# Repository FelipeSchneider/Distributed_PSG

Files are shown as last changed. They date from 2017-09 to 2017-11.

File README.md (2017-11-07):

# Distributed_PSG
Final project of the Electrical Engineering course, made by Felipe Britto Azevedo Schneider. The goal of this project is to develop hardware and software capable of monitoring a patient thought the night with more comfort that is possible using the traditional method.
Article abstract:
The impairment of sleep quality directly rises the chances of heart attack, obesity, and strokes, among others, what makes the polysomnography (PSG) an important public health tool. However, the inherent problems with PSG makes the correct diagnosis of sleep diseases a difficult task. This work presents a distributed novel class III PSG system, composed of three boards, all together capable of monitoring simultaneously environmental variables and patient signals. This system reduces the distress of a PSG exam, dismiss the need for an overnight sleep in a health care/sleep center, facilitates a self-set-up and an internet based diagnosis. Methods: Design and implementation of two wearable and one bedside PCB boards that together are able to, synchronously, monitor, process and log into a microSD card environmental parameters (temperature, humidity, visible light intensity and audible noise level) together with patient signals (electrocardiogram, electrooculogram, body, and limbs position). Results: A novel class III PSG system with independent boards capable of operating for more than 16 hours powered by a 750 mAh, 3.7 V battery with 0.003% data loss during preliminary PSG exams. Additionally, a computer-based program capable of reading, decode and present the data in graphs was developed and is presented. Conclusion: This article contributes to the PSG research and with the development of new PSG systems as well as the improvement of patients comfort. All code and hardware here developed are open.

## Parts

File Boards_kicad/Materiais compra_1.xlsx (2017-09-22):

MOUSER OU DIGIKEY |  |  |  |  | COMPRA NO BRASIL / JÁ COMPRADO ALIEXPRESS |  |  |  |  | AMOSTRA TEXAS
Encapsulamento | Quantity | Designation | Preço un | Total | Encapsulamento | Quantity | Designation | Preço un | Total | Encapsulamento | Quantity | Designation | Preço un | Total
TQFP-100_14x14mm_Pitch0.5mm | 1 | ATXMEGA128A1U-A |  |  | Pin_Header2x05 | 3 | PORT A |  |  | SC-70-5 | 1 | TPS71727
 |  |  |  |  | Pin_Header2x02 | 1 | CONN_02X02 |  |  | SC-70-5 | 1 | TPS71733
 |  |  |  |  | Pin_Header2x03 | 1 | PDI |  |  | ADXL335 | 1 | ADXL335
 |  |  |  |  | Pin_Header1x02 | 5 | CONN_01X02 |  |  | ADS1293 | 1 | ADS1293
 |  |  |  |  | Pin_Header1x10 | 1 | nRF8001 CON |  |  | HDC1000 | 1 | HDC1000
R_0603 | 4 | 1K2 |  |  |  |  |  |  |  | OPT3001 | 1 | OPT3001
R_0603 | 3 | 47k
R_0603 | 2 | 15k |  |  | TO-92 | 2 | LM35
R_0603 | 8 | 10K
R_0603 | 1 | 8k2
R_0603 | 4 | 220 |  |  | Trimpot | 1 | 100k
R_0603 | 3 | 1M
R_0603 | 1 | 120k |  |  | LDR | 1 | LDR
R_0603 | 6 | 100k
R_0603 | 1 | 12k |  |  | J2-connector | 3 | MIC-CON-MONO
R_0603 | 1 | 180k |  |  | 5mm-smd-button | 1 | SW_PUSH
R_0603 | 2 | 10k |  |  | 4.5mm-dip-button | 1 | SW_PUSH
R_0603 | 1 | 22k
C_0603 | 5 | 10nF |  |  | Diode_DO-35 | 1 | D_Schottky
C_0603 | 15 | 100n |  |  | Diode_DO-41 | 2 | D_Schottky
C_0603 | 4 | 10uF |  |  | Eletret-mic-6x5 | 1 | Electret-mic
C_0603 | 7 | 1uF
C_0603 | 3 | 10u
C_0603 | 2 | 22p |  |  |  |  |  |  |  | DBV-PDSO-G6 | 1 | LM2665
C_0603 | 1 | 1u |  |  |  |  |  |  |  | SOIC8-PDSO_G8 | 1 | opa2333
C_0603 | 2 | 100nF
C_0603 | 6 | Xn
C_0603 | 1 | 1.5n
C_0603 | 3 | 3u3
C_0603 | 1 | 16pF
C_0603 | 2 | 2u2F
C_0603 | 2 | 1u5F
Diode_DO-35_SOD27_Horizontal_RM10 | 1 | Z 5.7V
LED_0603 | 4 | LED
uSD_5027_normal | 1 | uSD
Crystal_HC49-U_Vertical | 1 | 4.096MHz
R_0805 | 2 | FILTER

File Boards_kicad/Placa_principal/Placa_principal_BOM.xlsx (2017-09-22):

Id | Designator | Package | Quantity | Designation | Supplier and ref | posicionados
1 | R25 | R_0603 | 1 | 100K |  | R25
2 | R19,R22,R23,R24 | R_0603 | 4 | 1K2 |  | R19, R22
3 | ,, | 1pin | 3
4 | P4 | Pin_Header_Straight_2x05 | 1 | PORT A
5 | C16,C2,C5,C13,C33 | C_0603 | 5 | 10nF |  | C2,C5,C22
6 | C37,C22,C23,C32,C35,C36,C38,C39,C40,C41,C42,C43,C44,C45,C46 | C_0603 | 15 | 100n |  | C35,C23,C32
7 | P6 | Pin_Header_Straight_2x05 | 1 | PORT D
8 | U3,U1 | TO-92_Molded_Narrow_Oval | 2 | LM35
9 | X1 | Crystal_HC49-U_Vertical | 1 | 4.096MHz
10 | IC1 | TQFP-100_14x14mm_Pitch0.5mm | 1 | ATXMEGA128A1U-A
11 | C9,C10,C14,C17 | C_0603 | 4 | 10uF
12 | C1,C3,C4,C6,C7,C8,C15 | C_0603 | 7 | 1uF |  | C1,C3,C4,C6,C7
13 | C11,C12,C20 | C_0603 | 3 | 10u |  | C20
14 | C18,C19 | C_0603 | 2 | 22p |  | C18,C19
15 | C21 | C_0603 | 1 | 1u
16 | C24,C25 | C_0603 | 2 | 100nF
17 | C26,C27,C28,C29,C30,C31 | C_0603 | 6 | Xn
18 | C34 | C_0603 | 1 | 1.5n |  | C34
19 | D1 | Diode_DO-35_SOD27_Horizontal_RM10 | 1 | Z 5.7V
20 | D2,D3,D4,D5 | LED_0603 | 4 | LED |  | D2,D3,D4,D5
21 | FB1,FB2 | R_0805 | 2 | FILTER
22 | P1 | Pin_Header_Straight_2x02 | 1 | CONN_02X02
23 | P3 | Pin_Header_Straight_2x03 | 1 | PDI
24 | P5 | Pin_Header_Straight_2x05 | 1 | PORT J
25 | P8 | Pin_Header_Straight_1x10 | 1 | nRF8001 CON
26 | R1,R2,R33 | R_0603 | 3 | 47k
27 | R3,R4 | R_0603 | 2 | 15k
28 | R5,R12,R13,R14,R15,R16,R17,R26 | R_0603 | 8 | 10K |  | R12,R13,R14,R15,R16,R17
29 | R7 | R_0603 | 1 | 8k2
30 | R8,R9,R10,R11 | R_0603 | 4 | 220 |  | R8,R9,R10,R11
31 | R18,R20,R21 | R_0603 | 3 | 1M |  | R18,R21
32 | U2 | SC-70-5 | 1 | TPS71727
33 | U4 | SC-70-5 | 1 | TPS71733
34 | U5 | ADXL335 | 1 | ADXL335 |  | X
35 | U6 | ADS1293 | 1 | ADS1293 |  | X
36 | U7 | HDC1000 | 1 | HDC1000 |  | X
37 | U8 | OPT3001 | 1 | OPT3001
38 | VR1 | Pin_Header_Straight_1x03 | 1 | 100k
39 | P15,P12,P13,P14,P16 | Pin_Header_Straight_1x02 | 5 | CONN_01X02
40 | R6 | Pin_Header_Straight_1x02 | 1 | LDR
41 | SD1 | uSD_5027_normal | 1 | uSD |  | SD1
42 | P9,P10,P11 | J2-connector | 3 | MIC-CON-MONO |  | P9,P10,P11
43 | SW1 | 5mm-smd-button | 1 | SW_PUSH |  | SW1
44 | SW2 | 4.5mm-dip-button | 1 | SW_PUSH |  | SW2
45 | C47,C48,C49 | C_0603 | 3 | 3u3 |  | c47,c49
46 | C50 | C_0603 | 1 | 16pF |  | C50
47 | C51,C54 | C_0603 | 2 | 2u2F |  | C51,C54
48 | C52,C53 | C_0603 | 2 | 1u5F |  | C52,C53
49 | D6 | Diode_DO-35_SOD27_Horizontal_RM10 | 1 | D_Schottky
50 | D7,D8 | Diode_DO-41_SOD81_Vertical_AnodeUp | 2 | D_Schottky
51 | MK1 | Eletret-mic-6x5 | 1 | Electret-mic
52 | R27 | R_0603 | 1 | 120k
53 | R28,R29,R30,R32,R36 | R_0603 | 5 | 100k
54 | R31 | R_0603 | 1 | 12k
55 | R34 | R_0603 | 1 | 180k
56 | R35,R38 | R_0603 | 2 | 10k
57 | R37 | R_0603 | 1 | 22k
58 | U9 | DBV-PDSO-G6 | 1 | LM2665
59 | U10 | SOIC8-PDSO_G8 | 1 | opa2333

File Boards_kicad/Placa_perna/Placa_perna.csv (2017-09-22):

Id | Designator | Package | Quantity | Designation | Supplier and ref
1 | C1,C2,C4,C7,C9 | C_0603 | 5 | 1uF
2 | C3,C6 | C_0603 | 2 | 10nF
3 | C10 | C_0603 | 1 | 10u
4 | C11 | C_0603 | 1 | 100nF
5 | C12,C13,C14 | C_0603 | 3 | 100n
6 | D1 | Diode_DO-35_SOD27_Horizontal_RM10 | 1 | Z 5.7V
7 | D2,D3 | LED_0603 | 2 | LED
8 | P1,P5 | Pin_Header_Straight_1x02 | 2 | CONN_01X02
9 | P3 | Pin_Header_Straight_2x03 | 1 | PDI
10 | P4 | 4-pin-50mil | 1 | CONN_01X04
11 | P6 | Pin_Header_Straight_1x10 | 1 | nRF8001 CON
12 | R1,R3 | R_0603 | 2 | 47k
13 | R4 | R_0603 | 1 | 10K
14 | R5,R6 | R_0603 | 2 | 220
15 | SD1 | uSD_5027_normal | 1 | uSD
16 | SW1 | 5mm-smd-button | 1 | SW_PUSH
17 | U2 | SC-70-5 | 1 | TPS71733
18 | U3 | SC-70-5 | 1 | TPS71727
19 | U4 | ADXL335 | 1 | ADXL335
20 | IC1 | TQFP-44_10x10mm_Pitch0.8mm | 1 | ATXMEGA128A4U-A
21 | P2 | 2x2-pin-50mil | 1 | CONN_02X02
22 | , | 1pin-mod | 2 | 1pin

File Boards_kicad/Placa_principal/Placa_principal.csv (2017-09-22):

Id | Designator | Package | Quantity | Designation | Supplier and ref
1 | C14,C9,C10,C17,C58 | C_0603 | 5 | 10uF
2 | U7 | HDC1050 | 1 | HDC1050
3 | C34 | C_0603 | 1 | 1.5n
4 | R25 | R_0603 | 1 | 100K
5 | R19,R22,R5,R12,R13,R14,R15,R16,R17,R23,R24,R26 | R_0603 | 12 | 10K
6 | P4 | Pin_Header_Straight_2x05 | 1 | PORT B
7 | C16,C2,C5,C13,C33 | C_0603 | 5 | 10nF
8 | C37,C22,C23,C32,C35,C36,C38,C39,C40,C41,C42,C43,C44,C45,C46,C56,C57 | C_0603 | 17 | 100n
9 | P6 | Pin_Header_Straight_2x05 | 1 | PORT D
10 | U3,U1 | TO-92_Molded_Narrow_Oval | 2 | LM35
11 | X1 | Crystal_HC49-U_Vertical | 1 | 4.096MHz
12 | IC1 | TQFP-100_14x14mm_Pitch0.5mm | 1 | ATXMEGA128A1U-A
13 | C1,C3,C4,C6,C7,C8,C15 | C_0603 | 7 | 1uF
14 | C11,C12,C20 | C_0603 | 3 | 10u
15 | C18,C19 | C_0603 | 2 | 22p
16 | C21 | C_0603 | 1 | 1u
17 | C24,C25 | C_0603 | 2 | 100nF
18 | C26,C27,C28,C29,C30,C31 | C_0603 | 6 | Xn
19 | D2,D3,D4,D5 | LED_0603 | 4 | LED
20 | P1 | Pin_Header_Straight_2x02 | 1 | CONN_02X02
21 | P3 | Pin_Header_Straight_2x03 | 1 | PDI
22 | P5 | Pin_Header_Straight_2x05 | 1 | PORT J
23 | P8 | Pin_Header_Straight_1x10 | 1 | nRF8001 CON
24 | R1,R2,R33 | R_0603 | 3 | 47k
25 | R3,R4 | R_0603 | 2 | 15k
26 | R7 | R_0603 | 1 | 8k2
27 | R8,R9,R10,R11 | R_0603 | 4 | 220
28 | R18,R20,R21,R39 | R_0603 | 4 | 1M
29 | U2 | SC-70-5 | 1 | TPS71727
30 | U4 | SC-70-5 | 1 | TPS71733
31 | U8 | OPT3001 | 1 | OPT3001
32 | VR1 | Pin_Header_Straight_1x03 | 1 | 100k
33 | R6 | Pin_Header_Straight_1x02 | 1 | LDR
34 | SD1 | uSD_5027_normal | 1 | uSD
35 | P9,P10,P11 | J2-connector | 3 | MIC-CON-MONO
36 | P12,P13,P14,P16,P2 | Pin_Header_Straight_1x02 | 5 | CONN_01X02
37 | SW1 | 5mm-smd-button | 1 | SW_PUSH
38 | SW2 | 4.5mm-dip-button | 1 | SW_PUSH
39 | C47,C48,C49 | C_0603 | 3 | 3u3
40 | C50 | C_0603 | 1 | 16pF
41 | C51,C54 | C_0603 | 2 | 2u2F
42 | C52,C53 | C_0603 | 2 | 1u5F
43 | D6 | Diode_DO-35_SOD27_Horizontal_RM10 | 1 | D_Schottky
44 | D7,D8 | Diode_DO-41_SOD81_Vertical_AnodeUp | 2 | D_Schottky
45 | R27 | R_0603 | 1 | 120k
46 | R28,R29,R30,R32,R36 | R_0603 | 5 | 100k
47 | R31 | R_0603 | 1 | 12k
48 | R34 | R_0603 | 1 | 180k
49 | R35,R38 | R_0603 | 2 | 10k
50 | R37 | R_0603 | 1 | 22k
51 | U9 | DBV-PDSO-G6 | 1 | LM2665
52 | U10 | SOIC8-PDSO_G8 | 1 | opa2333
53 | FB1,FB2 | R_1206 | 2 | FILTER
54 | U5 | ADXL335_correto | 1 | ADXL335
55 | U6 | ADS1293-correto | 1 | ADS1293
56 | MK1 | Eletret-mic-6x5 | 1 | Electret-mic
57 | P15 | Pin_Header_Angled_1x02 | 1 | CONN_01X02
58 | D1 | Diode_DO-41_SOD81_Vertical_KathodeUp | 1 | Z 5.7V
59 | C55 | c_elec_6.3x7.7 | 1 | 47uF
60 | X2 | CRISTAL_16Mhz | 1 | CRISTAL_16MHz

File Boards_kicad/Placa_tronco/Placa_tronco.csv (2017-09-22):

Id | Designator | Package | Quantity | Designation | Supplier and ref
1 | C1,C3,C4,C6,C7,C8 | C_0603 | 6 | 1uF
2 | C2,C5,C11,C30 | C_0603 | 4 | 10nF
3 | C9,C10,C17 | C_0603 | 3 | 10u
4 | C12 | C_0603 | 1 | 10uF
5 | C15,C16 | C_0603 | 2 | 22p
6 | C18 | C_0603 | 1 | 1u
7 | C19,C20,C29,C32,C33,C34,C35,C36,C37,C38,C39,C40,C41 | C_0603 | 13 | 100n
8 | C21,C22 | C_0603 | 2 | 100nF
9 | C23,C24,C25,C26,C27,C28 | C_0603 | 6 | Xn
10 | C31 | C_0603 | 1 | 1.5n
11 | D1 | Diode_DO-35_SOD27_Horizontal_RM10 | 1 | Z 5.7V
12 | D2,D3 | LED_0603 | 2 | LED
13 | FB1,FB2 | R_0805 | 2 | FILTER
14 | IC1 | TQFP-100_14x14mm_Pitch0.5mm | 1 | ATXMEGA128A1U-A
15 | P1 | Connector_Molex_PicoBlade_53048-0210 | 1 | CONN_01X02
16 | P2 | Pin_Header_Straight_2x02 | 1 | CONN_02X02
17 | P3 | Pin_Header_Straight_2x03 | 1 | PDI
18 | P4,P5 | 5-pin-50mil | 2 | Acelerometro
19 | P6,P7,P8,P9 | Pin_Header_Straight_1x02 | 4 | CONN_01X02
20 | P10 | Pin_Header_Straight_1x10 | 1 | nRF8001 CON
21 | P11,P12,P13 | J2-connector | 3 | MIC-CON-MONO
22 | P14 | 4-pin-50mil | 1 | CONN_01X04
23 | R1,R2 | R_0603 | 2 | 47k
24 | R3,R6,R7,R8,R9,R10,R11 | R_0603 | 7 | 10K
25 | R4,R5 | R_0603 | 2 | 220
26 | R12,R13,R14 | R_0603 | 3 | 1M
27 | R15 | R_0603 | 1 | 100K
28 | SD1 | uSD_5027_normal | 1 | uSD
29 | SW1 | 5mm-smd-button | 1 | SW_PUSH
30 | U1 | SC-70-5 | 1 | TPS71727
31 | U2 | SC-70-5 | 1 | TPS71733
32 | U3 | ADXL335 | 1 | ADXL335
33 | U4 | ADS1293 | 1 | ADS1293
34 | X1 | Crystal_HC49-U_Vertical | 1 | 4.096MHz
35 | ,,, | 1pin-mod | 4 | 1pin

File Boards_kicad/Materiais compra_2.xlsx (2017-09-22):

MOUSER |  |  |  |  |  |  |  |  | JÁ COMPRADO/COMPRA NO BRASIL/ALIEXPRESS |  |  |  |  | AMOSTRA TEXAS
Encapsulamento | Part number | Link | Qnt | Qnt extra | Designation | Preço un | Total |  | Encapsulamento | Quantity | Designation | Preço un | Total | Encapsulamento | Quantity | Designation | Preço un | Total
TQFP-100_14x14mm_Pitch0.5mm | ATXMEGA128A1U-AU | Link (http://br.mouser.com/ProductDetail/Atmel/ATXMEGA128A1U-AU/) | 2 | 1 | ATXMEGA128A1U-A | 5.77 | 17.31 |  | Pin_Header2x05 | 3 | PORT A |  |  | SC-70-5 | 3 | TPS71727
TQFP-44_10x10mm_Pitch0.8mm | ATXMEGA128A4U-AUR | Link (http://br.mouser.com/ProductDetail/Atmel/ATXMEGA128A4U-AUR/?qs=sGAEpiMZZMvu0Nwh4cA1wUjPEYDIqicGdVsKdzUaElY%3d) | 1 | 1 | ATXMEGA128A4U-A | 5.28 | 10.56 |  | Pin_Header2x02 | 1 | CONN_02X02 |  |  | SC-70-5 | 3 | TPS71733
 |  |  |  |  |  |  |  |  | Pin_Header2x03 | 1 | PDI
 |  |  |  |  |  |  |  |  | Pin_Header1x02 | 5 | CONN_01X02 |  |  | ADS1293 | 2 | ADS1293
R_0603 | ERJ-3EKF2200V | Link (http://br.mouser.com/ProductDetail/Panasonic/ERJ-3EKF2200V/) | 8 | 12 | 220 | 0.015 | 0.3 |  | Pin_Header1x10 | 1 | nRF8001 CON |  |  | HDC1000 | 1 | HDC1000
R_0603 | ERJ-3EKF1201V | Link (http://br.mouser.com/ProductDetail/Panasonic/ERJ-3EKF1201V/) | 4 | 16 | 1K2 | 0.015 | 0.3 |  | TO-92 | 2 | LM35 |  |  | OPT3001 | 1 | OPT3001
R_0603 | ERJ-3EKF8201V | Link (http://br.mouser.com/ProductDetail/Panasonic/ERJ-3EKF8201V/) | 1 | 9 | 8k2 | 0.015 | 0.15 |  | Trimpot | 1 | 100k |  |  | DBV-PDSO-G6 | 1 | LM2665
R_0603 | ERJ-3EKF1002V | Link (http://br.mouser.com/ProductDetail/Panasonic/ERJ-3EKF1002V/) | 18 | 22 | 10K | 0.014 | 0.56 |  | LDR | 1 | LDR |  |  | SOIC8-PDSO_G8 | 1 | opa2333
R_0603 | RK73H1JTTD1202F | Link (http://br.mouser.com/ProductDetail/KOA-Speer/RK73H1JTTD1202F/?qs=sGAEpiMZZMtlubZbdhIBIO9rBsJxYTiOrt46wOml5q8%3d) | 1 | 9 | 12k | 0.013 | 0.13 |  | J2-connector | 3 | MIC-CON-MONO
R_0603 | ERJ-3EKF1502V | Link (http://br.mouser.com/ProductDetail/Panasonic/ERJ-3EKF1502V/) | 2 | 8 | 15k | 0.014 | 0.14 |  | 5mm-smd-button | 1 | SW_PUSH
R_0603 | ERJ-3EKF2202V | Link (http://br.mouser.com/ProductDetail/Panasonic/ERJ-3EKF2202V/) | 1 | 9 | 22k | 0.015 | 0.15 |  | 4.5mm-dip-button | 3 | SW_PUSH
R_0603 | ERJ-3EKF4702V | Link (http://br.mouser.com/ProductDetail/Panasonic/ERJ-3EKF4702V/) | 7 | 13 | 47k | 0.014 | 0.28 |  | ADXL335 | 6 | ADXL335
R_0603 | ERJ-3EKF1003V | Link (http://br.mouser.com/ProductDetail/Panasonic/ERJ-3EKF1003V/?qs=sGAEpiMZZMtlubZbdhIBIHcx2Q2RnT7KWGFKEyTNwFY%3d) | 7 | 13 | 100k | 0.014 | 0.28 |  | Diode_DO-35 | 1 | D_Schottky
R_0603 | ERJ-3EKF1203V | Link (http://br.mouser.com/ProductDetail/Panasonic/ERJ-3EKF1203V/) | 1 | 9 | 120k | 0.015 | 0.15 |  | Diode_DO-41 | 2 | D_Schottky
R_0603 | ERJ-3EKF1803V | Link (http://br.mouser.com/ProductDetail/Panasonic/ERJ-3EKF1803V/) | 1 | 9 | 180k | 0.015 | 0.15 |  | Eletret-mic-6x5 | 1 | Electret-mic
R_0603 | ERJ-3EKF1004V | Link (http://br.mouser.com/ProductDetail/Panasonic/ERJ-3EKF1004V/) | 6 | 14 | 1M | 0.014 | 0.28 |  | Cabos ECG
 |  |  |  |  |  |  |  |  | Bateria
 |  |  |  |  |  |  |  | 2.97 | Cartão uSD
C_0603 | GRM1885C1H160JA01D | Link (http://br.mouser.com/ProductDetail/Murata-Electronics/GRM1885C1H160JA01D/) | 1 | 9 | 16pF | 0.037 | 0.37
C_0603 | C0603C220J5GACTU | Link (http://br.mouser.com/ProductDetail/Kemet/C0603C220J5GACTU/?qs=sGAEpiMZZMs0AnBnWHyRQJIiGvDVk92VjMSB6bGXdCQ%3d) | 4 | 16 | 22p | 0.022 | 0.44
C_0603 | GRM188R71H102KA01D | Link (http://br.mouser.com/ProductDetail/Murata-Electronics/GRM188R71H102KA01D/) | 12 | 18 | 1n | 0.011 | 0.33
C_0603 | GCM188R71H152KA37D | Link (http://br.mouser.com/ProductDetail/Murata-Electronics/GCM188R71H152KA37D/) | 2 | 8 | 1.5n | 0.03 | 0.3
C_0603 | GRM188R71H103KA01D | Link (http://br.mouser.com/ProductDetail/Murata-Electronics/GRM188R71H103KA01D/?qs=sGAEpiMZZMs0AnBnWHyRQNOmsPzkISN05dIajb7qEY0%3d) | 11 | 19 | 10nF | 0.01 | 0.3
C_0603 | GRM188R71H104KA93D | Link (http://br.mouser.com/ProductDetail/Murata-Electronics/GRM188R71H104KA93D/) | 36 | 64 | 100n | 0.013 | 1.3
C_0603 | GRM188R61A105KA61D | Link (http://br.mouser.com/ProductDetail/Murata-Electronics/GRM188R61A105KA61D/?qs=sGAEpiMZZMs0AnBnWHyRQOK8EV8n4V50D9C2Dkl1Xe0%3d) | 20 | 80 | 1uF | 0.014 | 1.4
C_0603 | C1608X5R1E155K080AB | Link (http://br.mouser.com/ProductDetail/TDK/C1608X5R1E155K080AB/?qs=sGAEpiMZZMs0AnBnWHyRQFzBYxg9rzNcStMZ4xl0X30%3d) | 2 | 5 | 1u5F | 0.24 | 1.68
C_0603 | GRM188R61C225KE15D | Link (http://br.mouser.com/ProductDetail/Murata-Electronics/GRM188R61C225KE15D/?qs=sGAEpiMZZMs0AnBnWHyRQOK8EV8n4V50UN1W1GI6cUA%3d) | 2 | 8 | 2u2F | 0.064 | 0.64
C_0603 | GRM188R61A335KE15D | Link (http://br.mouser.com/ProductDetail/Murata-Electronics/GRM188R61A335KE15D/) | 3 | 7 | 3u3 | 0.09 | 0.9
C_0603 | GRM188R61A106KE69D | Link (http://br.mouser.com/ProductDetail/Murata-Electronics/GRM188R61A106KE69D/) | 12 | 18 | 10uF | 0.08 | 2.4
 |  |  |  |  |  |  |  | 9.85
conector uSD_5027 | 502774-0891 | Link (http://br.mouser.com/ProductDetail/Molex/502774-0891/) | 3 | 2 | uSD | 3.64 | 18.2
conector bateria | 53048-0210 | Link (http://br.mouser.com/ProductDetail/Molex/53048-0210/) | 3 | 2 | molex picoblade | 0.41 | 2.05
conector bateria fem | 51021-0200 | Link (http://br.mouser.com/ProductDetail/Molex/51021-0200/) | 3 | 3 | picoblade fem | 0.19 | 1.14
Wire housing | 50058-8100 | Link (http://br.mouser.com/ProductDetail/Molex/50058-8100/?qs=sGAEpiMZZMtVoztFdqDXO1VLAxqCp5qS) | 6 | 4 | Wire housing | 0.201 | 2.01
Diode_DO-35_SOD27_Horizontal_RM10 | 1N5232B | Link (http://br.mouser.com/ProductDetail/Fairchild-Semiconductor/1N5232B/) | 3 | 3 | Z 5.7V | 0.11 | 0.66
LED_0603 | LB Q39G-L2N2-35-1 | Link (http://br.mouser.com/ProductDetail/OSRAM-Opto-Semiconductors/LB-Q39G-L2N2-35-1/?qs=sGAEpiMZZMuCm2JlHBGefsr41A2gKzLGECzfSjGujyE%3d) | 8 | 12 | LED | 0.133 | 2.66
Crystal_HC49-U_Vertical | ABL-4.096MHZ-B2 | Link (http://br.mouser.com/ProductDetail/ABRACON/ABL-4096MHZ-B2/?qs=sGAEpiMZZMtgSs4ktXb8pnDdnwe3zNmx) | 2 | 2 | 4.096MHz | 0.39 | 1.56
R_0805 |  |  | 6 |  | FILTER
 |  |  |  |  |  |  | 69.08

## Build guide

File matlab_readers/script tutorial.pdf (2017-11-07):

The matlab_readers folder present in the git has 3 readers, one for each module, and 3 folders, where the files that are created by the modules should be copied.

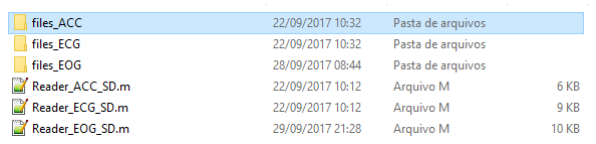
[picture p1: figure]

Reader_ACC_SD.m is responsible for read the files that come from the smallest module, the one that can be placed in the limbs. The Reader_ECG_SD.m reads the files from the board that should be placed in the chest; this board also has inputs to read data from 2 others 3-axis analogic accelerometers, the user just have to connect them to the board. The last script is responsible to read the files generated by the EOG module.

For each file, the first 3 letters identify the module (EOG, ECG or ACC). The number after the P identify the patient number, it starts from 1 if no files are found in the uSD card and goes up to 9. If there are files from 9 different patients, the patient number 1 is always overwrite. The last 2 numbers after the H represent the hour that the data was acquired, creating a logical sequence.

Opening the scripts, the user must change variables “paciente” (changing between the P number) and “hora” (changing the H number) to read different files.

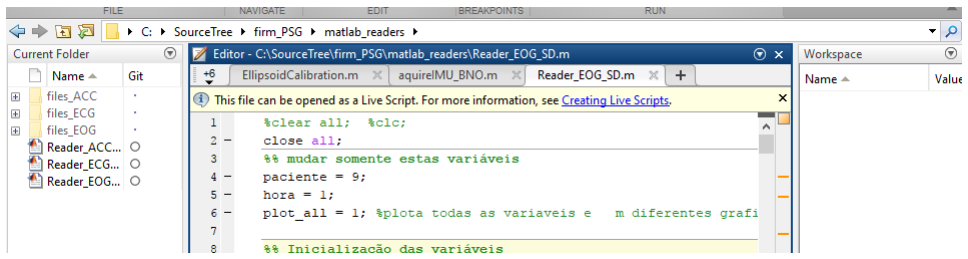
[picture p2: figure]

The reader also displays an error message if there is a second of information damaged.

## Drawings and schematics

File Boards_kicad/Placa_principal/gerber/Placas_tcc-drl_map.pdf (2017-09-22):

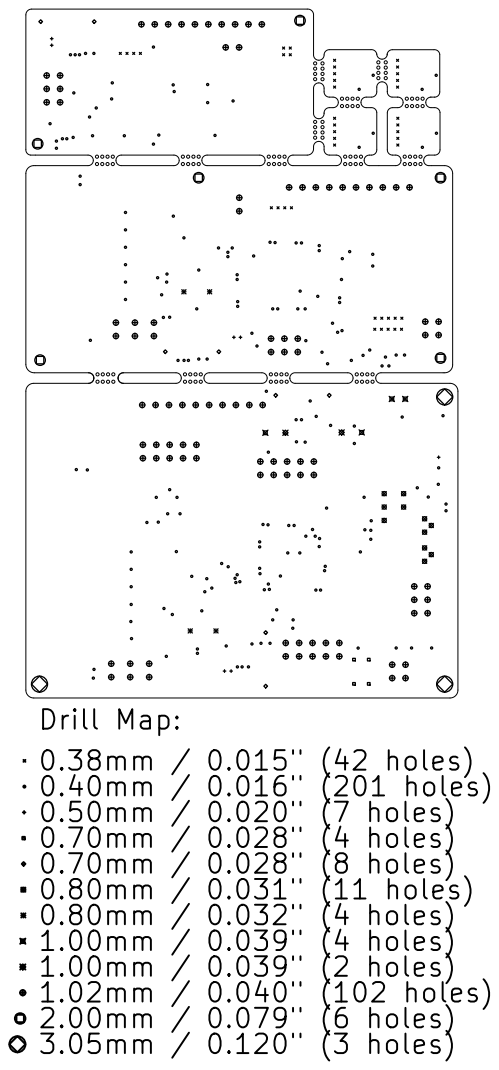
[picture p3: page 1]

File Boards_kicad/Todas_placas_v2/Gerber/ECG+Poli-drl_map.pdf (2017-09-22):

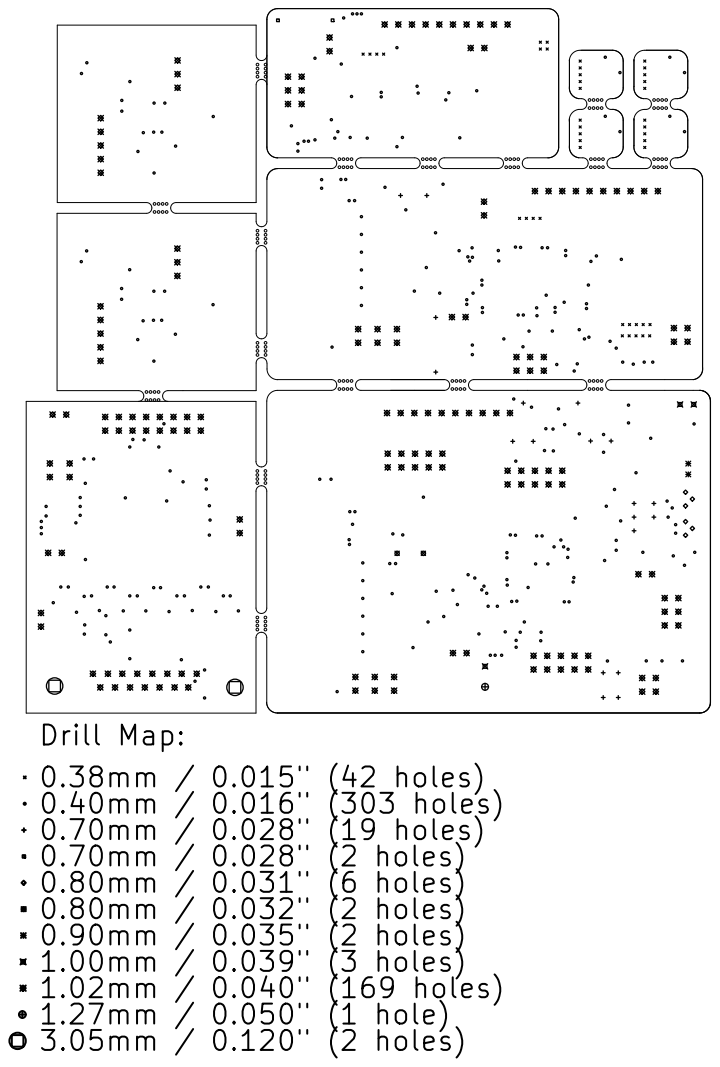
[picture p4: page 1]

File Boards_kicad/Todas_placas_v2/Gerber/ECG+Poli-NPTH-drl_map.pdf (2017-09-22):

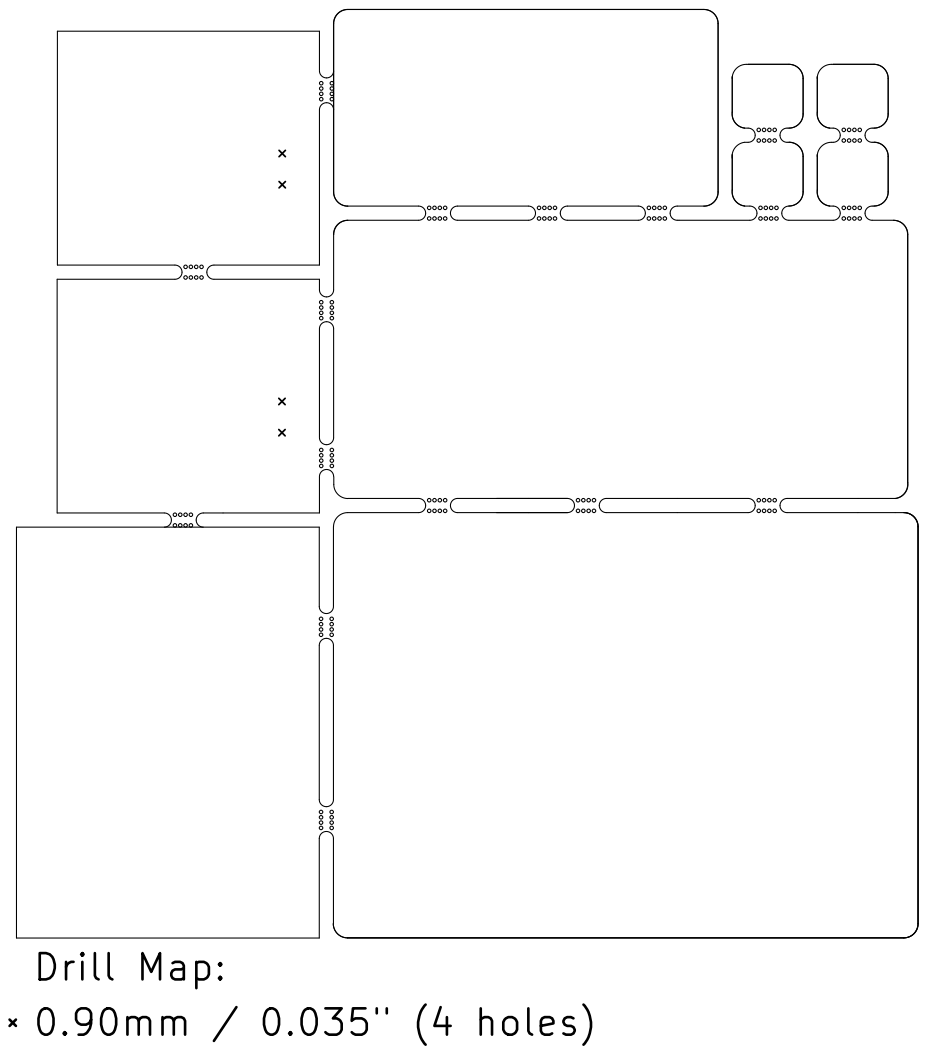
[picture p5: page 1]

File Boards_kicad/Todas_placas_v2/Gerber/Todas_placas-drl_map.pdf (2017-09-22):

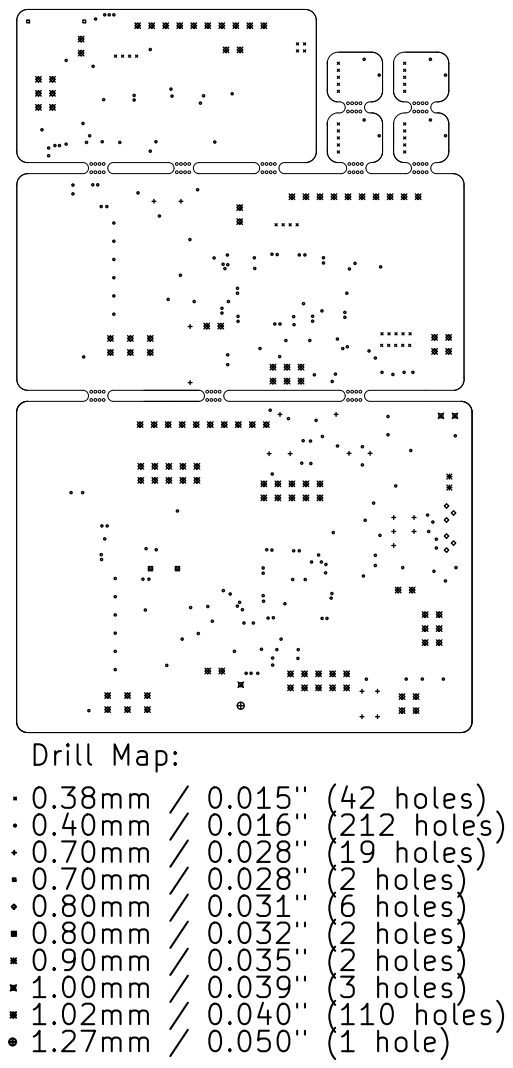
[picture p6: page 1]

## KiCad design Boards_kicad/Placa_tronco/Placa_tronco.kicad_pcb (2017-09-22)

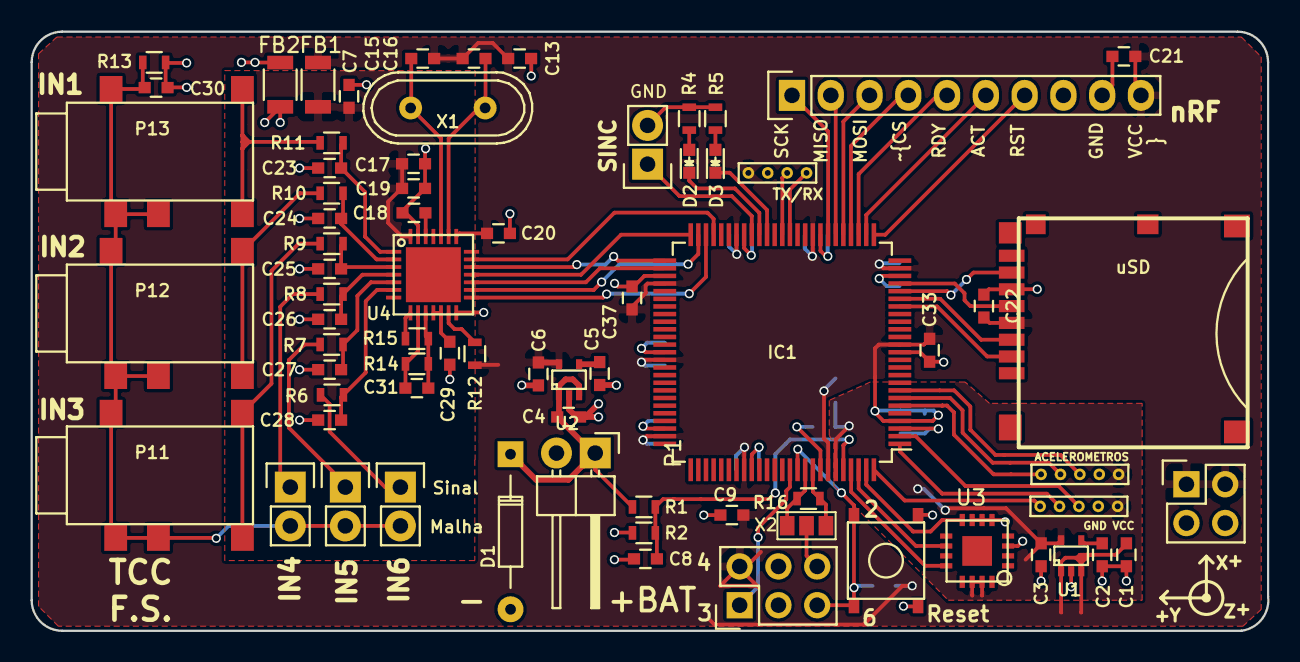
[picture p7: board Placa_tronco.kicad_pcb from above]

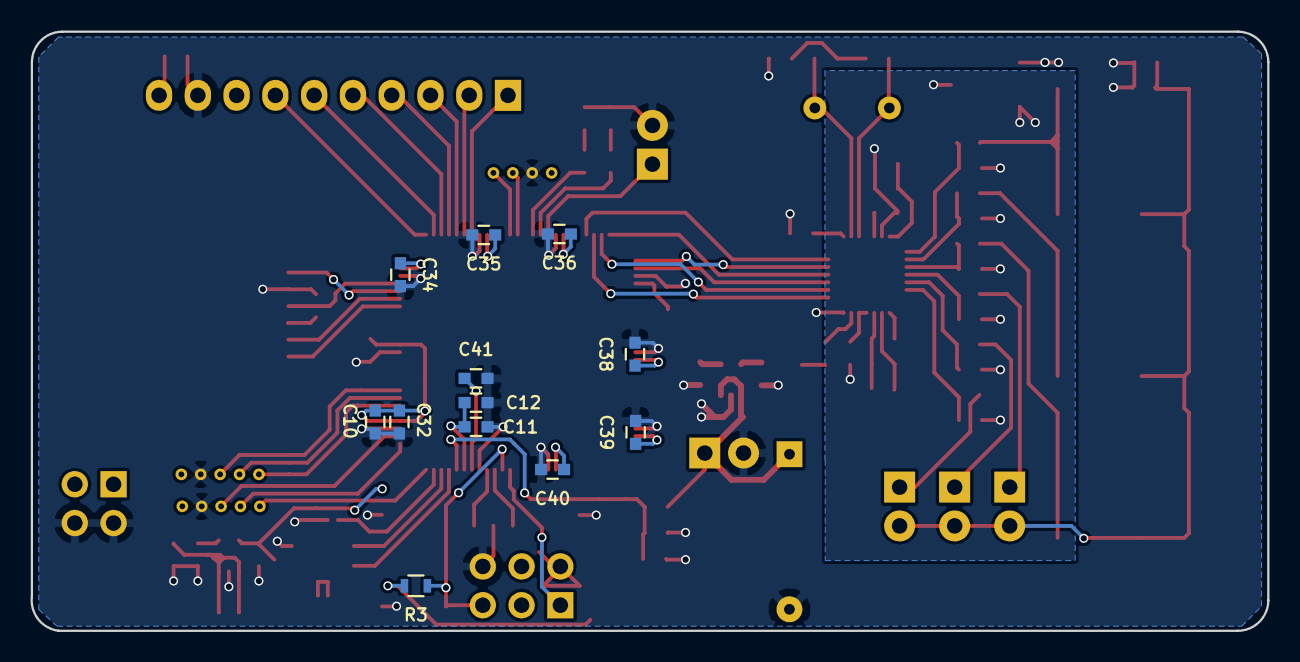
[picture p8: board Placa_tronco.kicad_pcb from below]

Board: 2 copper layers, 81.0 x 39.2 mm, 84 parts (12 on the bottom side), 67 nets.

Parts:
C1, C3, C4, C6, C7, C8: 1uF; C_0603
C2, C5, C11, C30: 10nF; C_0603
C9, C10, C17: 10u; C_0603
C12: 10uF; C_0603
C13, C19, C20, C29, C32, C33, C34, C35, C36, C37, C38, C39, C40, C41: 100n; C_0603
C15, C16: 22p; C_0603
C18: 1u; C_0603
C21, C22: 100nF; C_0603
C23, C24, C25, C26, C27, C28: Xn; C_0603
C31: 1.5n; C_0603
D1: Z 5.7V; Diode_DO-35_SOD27_Horizontal_RM10
D2, D3: LED; LED_0603
FB1, FB2: FILTER; R_1206
IC1: ATXMEGA128A1U-A; TQFP-100_14x14mm_Pitch0.5mm
P1: CONN_01X02; Pin_Header_Angled_1x02
P2: CONN_02X02; Pin_Header_Straight_2x02
P3: PDI; Pin_Header_Straight_2x03
P4, P5: Acelerometro; 5-pin-50mil
P6, P7, P8, P9: CONN_01X02; Pin_Header_Straight_1x02
P10: nRF8001 CON; Pin_Header_Straight_1x10
P11, P12, P13: MIC-CON-MONO; J2-connector
P14: CONN_01X04; 4-pin-50mil
R1, R2: 47k; R_0603
R3, R6, R7, R8, R9, R10, R11: 10K; R_0603
R4, R5: 220; R_0603
R12, R13, R14, R16: 1M; R_0603
R15: 100K; R_0603
SD1: uSD; uSD_5027_normal
SW1: SW_PUSH; 5mm-smd-button
U1: TPS71727; SC-70-5
U2: TPS71733; SC-70-5
U3: ADXL335; ADXL335_correto
U4: ADS1293; ADS1293-correto
X1: 4.096MHz; Crystal_HC49-U_Vertical
X2: CRISTAL_16MHz; CRISTAL_16Mhz

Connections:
+BAT: C4.2, D1.2, P1.1, R1.1, U2.1, U2.3
/ACT_nRF: IC1.27, P10.6
/ADCA_REF: C3.2, C11.2, C12.2, IC1.95, P4.1, P5.1, U1.5, U3.14, U3.15
/ADC_A1: C8.2, IC1.96, R1.2, R2.2
/ADC_A2: IC1.97, U3.12
/ADC_A3: IC1.98, U3.10
/ADC_A4: IC1.99, U3.8
/ADC_A5: IC1.100, P4.5
/ADC_A6: IC1.1, P4.4
/ADC_A7: IC1.2, P4.3
/ADC_B1: IC1.6, P5.5
/ADC_B2: IC1.7, P5.4
/ADC_B3: IC1.8, P5.3
/MISO_nRF: IC1.31, P10.2
/MISO_uSD: IC1.21, SD1.7
/MOSI-uSD: IC1.20, SD1.3
/MOSI_nRF: IC1.30, P10.3
/RDY_nRF: IC1.28, P10.5
/RESET: IC1.90, P3.5, R3.1, SW1.2
/RST_nRF: IC1.26, P10.7
/SCK-uSD: IC1.22, SD1.5
/SCK_nRF: IC1.32, P10.1
/malha: C30.2, P7.2, P8.2, P9.2, P11.1, P11.2, P11.5, P12.1, P12.2, P12.5, P13.1, P13.2, P13.5, R13.2
/xt1: IC1.91, R16.2, X2.1
/xt2: IC1.92, R16.1, X2.3
/~CS_nRF: IC1.29, P10.4
/~SS-uSD: IC1.19, SD1.2
GND: C1.1, C2.1, C3.1, C4.1, C5.1, C6.1, C8.1, C9.2, C10.2, C11.1, C12.1, C13.1, C20.2, C21.1, C22.1, C30.1, C32.2, C33.2, C34.2, C35.2, C36.2, C37.2, C38.2, C39.2, C40.2, C41.2, D1.1, FB2.1, IC1.3, IC1.13, IC1.23, IC1.33, IC1.43, IC1.53, IC1.63, IC1.73, IC1.84, IC1.93, P1.2, P2.3, P2.4, P3.6, P4.2, P5.2, P6.2, P10.9, P14.2, R2.1, R4.1, R5.1, R13.1, SD1.6, SW1.1, U1.2, U2.2, U3.3, U3.5, U3.6, U3.7, U4.14, X2.2
GNDA: C7.1, C17.2, C18.1, C19.2, C23.2, C24.2, C25.2, C26.2, C27.2, C28.2, C29.2, FB2.2, U4.27
unnamed: C2.2, U1.4
unnamed: C5.2, U2.4
unnamed: C15.2, U4.24, X1.2
unnamed: C16.2, U4.23, X1.1
unnamed: C18.2, U4.26
unnamed: C23.1, R11.1, U4.1
unnamed: C24.1, R10.1, U4.2
unnamed: C25.1, R9.1, U4.3
unnamed: C26.1, R8.1, U4.4
unnamed: C27.1, R7.1, U4.5
unnamed: C28.1, R6.1, U4.6
unnamed: C29.1, U4.11, U4.12
unnamed: C31.1, R14.1, R15.1, U4.10
unnamed: C31.2, R14.2, U4.9
unnamed: D2.1, IC1.41
unnamed: D2.2, R4.2
unnamed: D3.1, IC1.40
unnamed: D3.2, R5.2
unnamed: IC1.37, P14.4
unnamed: IC1.38, P14.3
unnamed: IC1.42, P6.1
unnamed: IC1.47, U4.20
unnamed: IC1.48, U4.15
unnamed: IC1.49, U4.16
unnamed: IC1.50, U4.18
unnamed: IC1.51, U4.19
unnamed: IC1.52, U4.17
unnamed: IC1.89, P3.1
unnamed: P7.1, R6.2
unnamed: P8.1, R7.2
unnamed: P9.1, R8.2
unnamed: P11.3, P11.4, R9.2
unnamed: P12.3, P12.4, R10.2
unnamed: P13.3, P13.4, R11.2
unnamed: R12.2, U4.13
unnamed: R15.2, U4.8
VCC: C1.2, C6.2, C9.1, C10.1, C13.2, C15.1, C16.1, C20.1, C21.2, C22.2, C32.1, C33.1, C34.1, C35.1, C36.1, C37.1, C38.1, C39.1, C40.1, C41.1, FB1.1, IC1.4, IC1.14, IC1.24, IC1.34, IC1.44, IC1.54, IC1.64, IC1.74, IC1.83, IC1.94, P2.1, P2.2, P3.2, P10.10, P14.1, R3.2, R12.1, SD1.4, U1.1, U1.3, U2.5, U4.22
aVDD: C7.2, C17.1, C19.1, FB1.2, U4.28

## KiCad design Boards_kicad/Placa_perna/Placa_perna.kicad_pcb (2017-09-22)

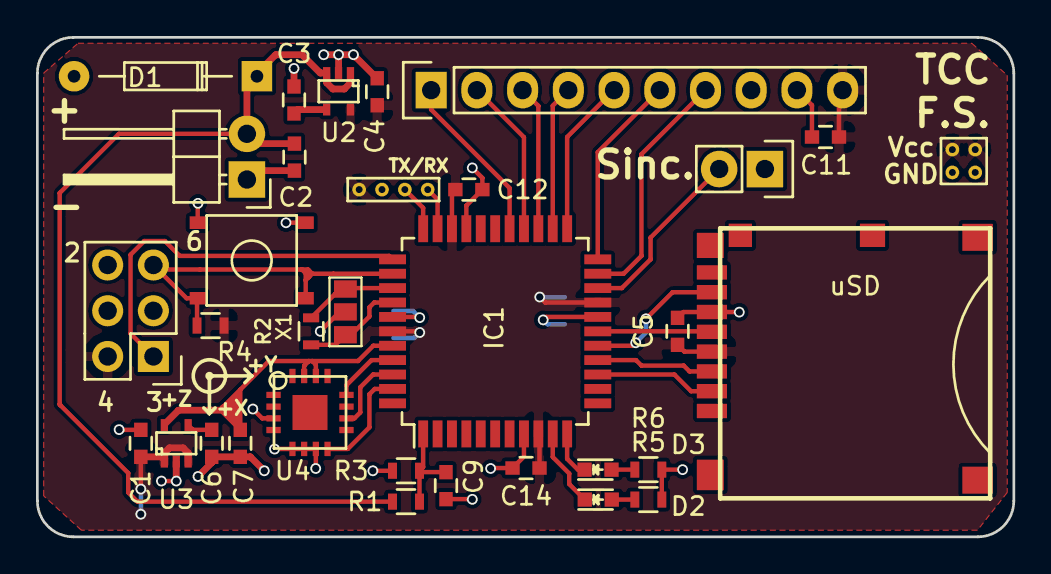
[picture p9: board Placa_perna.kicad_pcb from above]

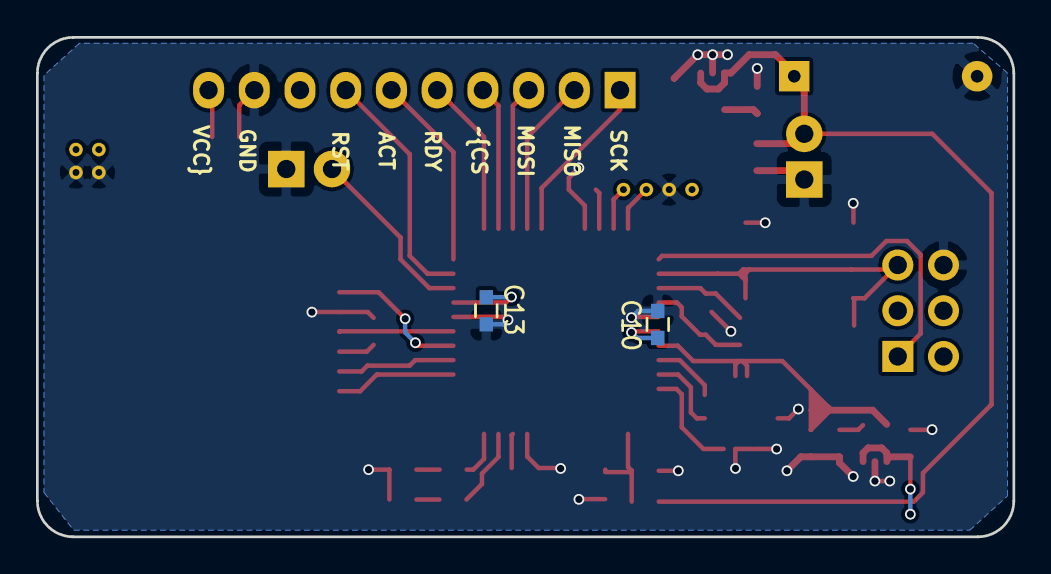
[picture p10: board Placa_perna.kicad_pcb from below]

Board: 2 copper layers, 54.2 x 27.8 mm, 35 parts (2 on the bottom side), 32 nets.

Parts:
C1, C2, C4, C7, C9: 1uF; C_0603
C3, C6: 10nF; C_0603
C5, C12, C13, C14: 100n; C_0603
C10: 10u; C_0603
C11: 100nF; C_0603
D1: Z 5.7V; Diode_DO-35_SOD27_Horizontal_RM10
D2, D3: LED; LED_0603
IC1: ATXMEGA128A4U-A; TQFP-44_10x10mm_Pitch0.8mm
P1: CONN_01X02; Pin_Header_Angled_1x02
P2: CONN_02X02; 2x2-pin-50mil
P3: PDI; Pin_Header_Straight_2x03
P4: CONN_01X04; 4-pin-50mil
P5: CONN_01X02; Pin_Header_Straight_1x02
P6: nRF8001 CON; Pin_Header_Straight_1x10
R1, R3: 47k; R_0603
R2: 1M; R_0603
R4: 10K; R_0603
R5, R6: 220; R_0603
SD1: uSD; uSD_5027_normal
SW1: SW_PUSH; 5mm-smd-button
U2: TPS71733; SC-70-5
U3: TPS71727; SC-70-5
U4: ADXL335; ADXL335_correto
X1: CRISTAL_16MHz; CRISTAL_16Mhz

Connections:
+BAT: C2.2, D1.2, P1.2, R1.1, U2.1, U2.3
/ACT_nRF: IC1.22, P6.6
/ADCA_REF: C7.2, IC1.40, U3.5, U4.14, U4.15
/ADC_A1: IC1.41, U4.12
/ADC_A2: IC1.42, U4.10
/ADC_A3: IC1.43, U4.8
/ADC_A5: C9.2, IC1.1, R1.2, R3.2
/MISO_nRF: IC1.26, P6.2
/MISO_uSD: IC1.16, SD1.7
/MOSI-uSD: IC1.15, SD1.3
/MOSI_nRF: IC1.25, P6.3
/RDY_nRF: IC1.23, P6.5
/RESET: IC1.35, P3.5, R4.1, SW1.2
/RST_nRF: IC1.21, P6.7
/SCK-uSD: IC1.17, SD1.5
/SCK_nRF: IC1.27, P6.1
/xt1: IC1.36, R2.2, X1.1
/xt2: IC1.37, R2.1, X1.3
/~CS_nRF: IC1.24, P6.4
/~SS-uSD: IC1.14, SD1.2
GND: C1.1, C2.1, C3.1, C4.1, C5.2, C6.1, C7.1, C9.1, C10.2, C11.1, C12.2, C13.2, C14.2, D1.1, IC1.8, IC1.18, IC1.30, IC1.38, P1.1, P2.3, P2.4, P3.6, P4.2, P5.1, P6.9, R3.1, R5.1, R6.1, SD1.6, SW1.1, U2.2, U3.2, U4.3, U4.5, U4.6, U4.7, X1.2
unnamed: C3.2, U2.4
unnamed: C6.2, U3.4
unnamed: D2.1, IC1.10
unnamed: D2.2, R5.2
unnamed: D3.1, IC1.11
unnamed: D3.2, R6.2
unnamed: IC1.20, P5.2
unnamed: IC1.32, P4.4
unnamed: IC1.33, P4.3
unnamed: IC1.34, P3.1
VCC: C1.2, C4.2, C5.1, C10.1, C11.2, C12.1, C13.1, C14.1, IC1.9, IC1.19, IC1.31, IC1.39, P2.1, P2.2, P3.2, P4.1, P6.10, R4.2, SD1.4, U2.5, U3.1, U3.3

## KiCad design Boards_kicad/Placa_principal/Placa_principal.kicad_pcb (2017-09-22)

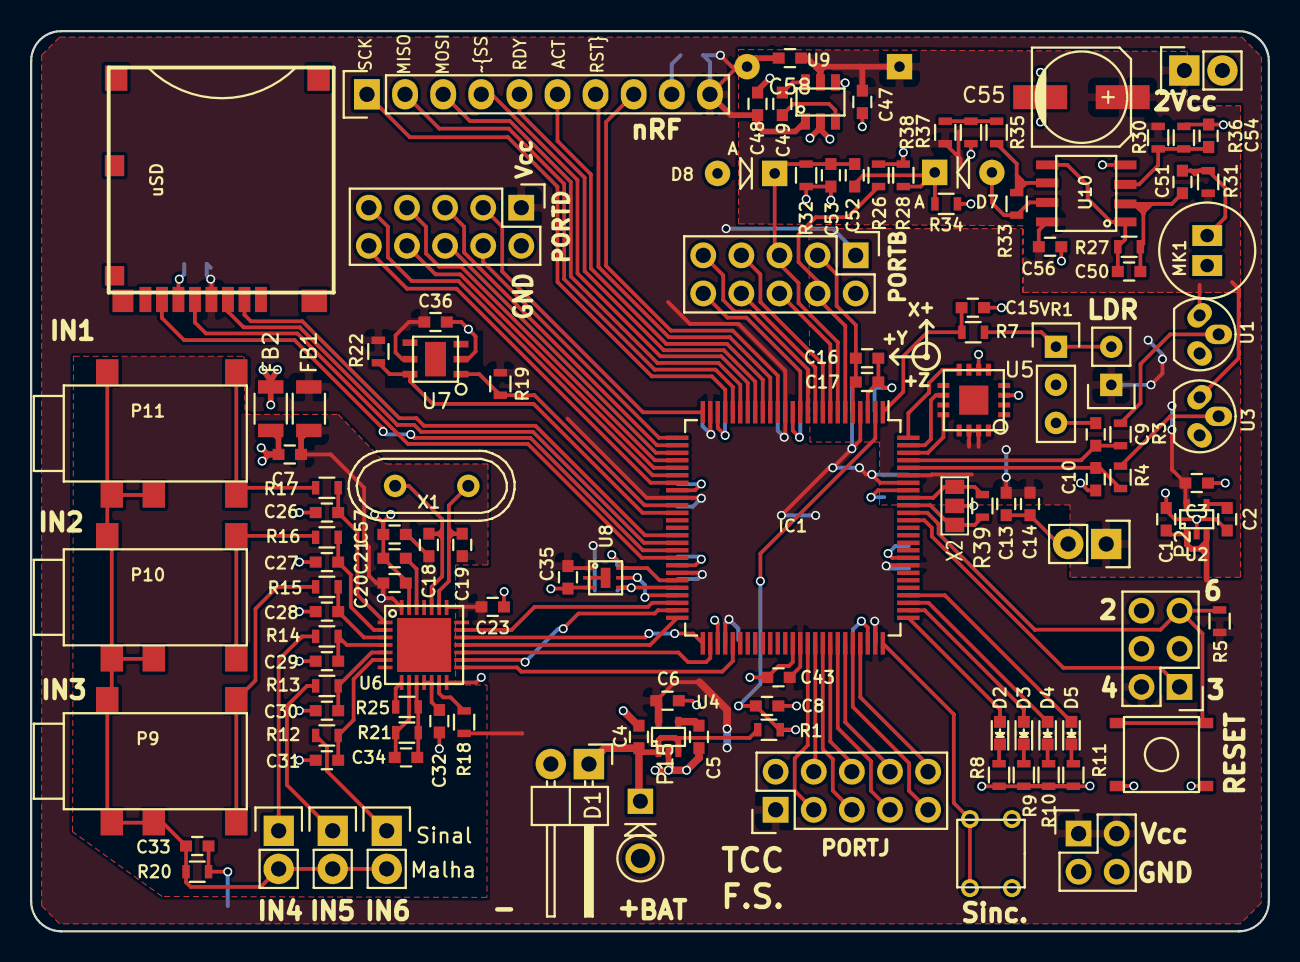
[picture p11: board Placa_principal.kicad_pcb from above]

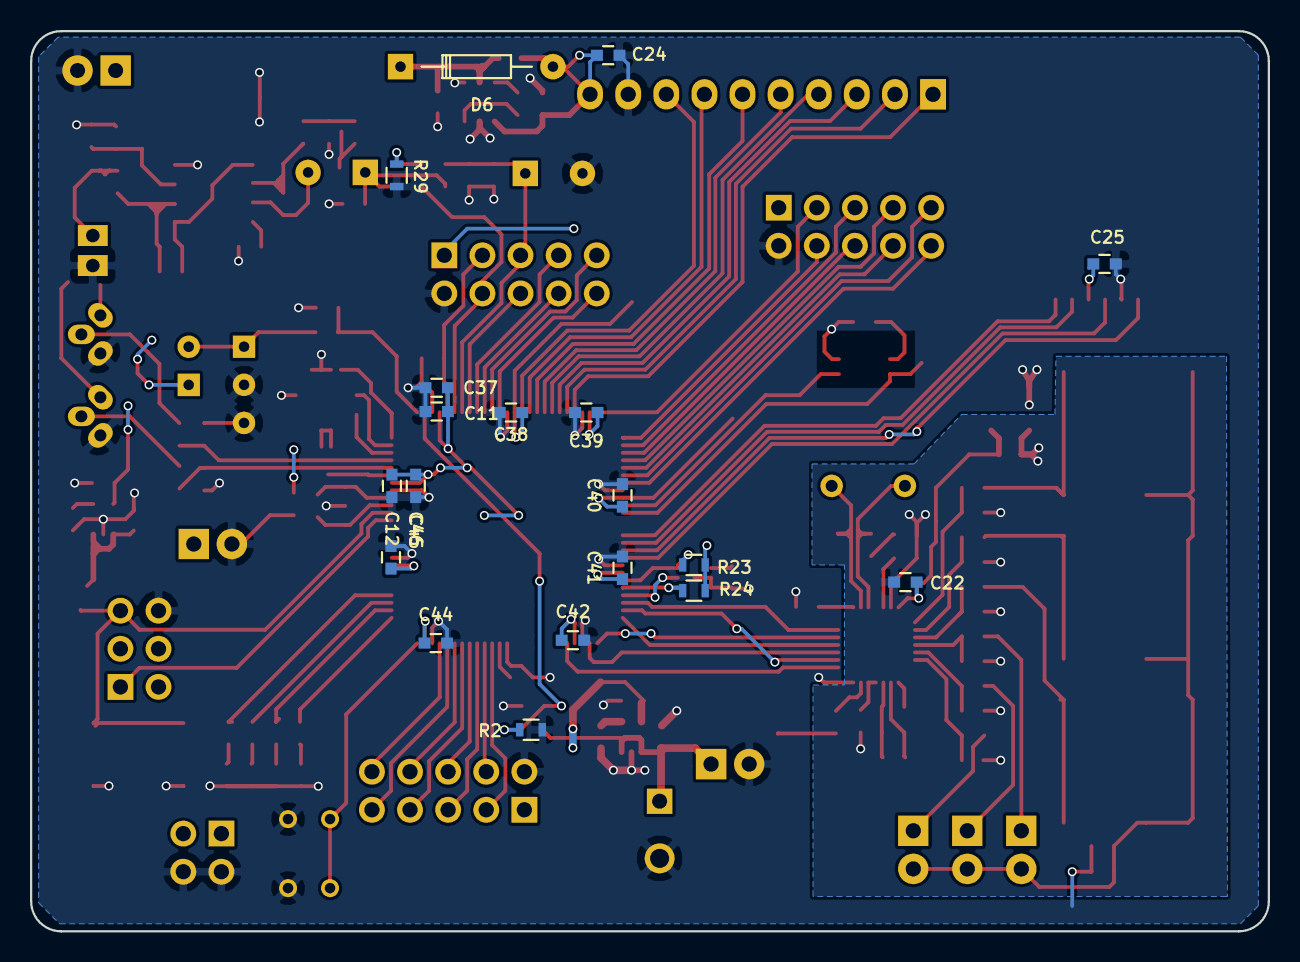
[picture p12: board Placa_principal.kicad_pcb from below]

Board: 2 copper layers, 82.5 x 60.0 mm, 140 parts (19 on the bottom side), 111 nets.

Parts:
C1, C3, C4, C6, C7, C8, C15: 1uF; C_0603
C2, C5, C13, C16, C33: 10nF; C_0603
C9, C10, C14, C17, C58: 10uF; C_0603
C11, C12, C20: 10u; C_0603
C18, C19: 22p; C_0603
C21: 1u; C_0603
C22, C23, C32, C35, C36, C37, C38, C39, C40, C41, C42, C43, C44, C45, C46, C56, C57: 100n; C_0603
C24, C25: 100nF; C_0603
C26, C27, C28, C29, C30, C31: Xn; C_0603
C34: 1.5n; C_0603
C47, C48, C49: 3u3; C_0603
C50: 16pF; C_0603
C51, C54: 2u2F; C_0603
C52, C53: 1u5F; C_0603
C55: 47uF; c_elec_6.3x7.7
D1: Z 5.7V; Diode_DO-41_SOD81_Vertical_KathodeUp
D2, D3, D4, D5: LED; LED_0603
D6: D_Schottky; Diode_DO-35_SOD27_Horizontal_RM10
D7, D8: D_Schottky; Diode_DO-41_SOD81_Vertical_AnodeUp
FB1, FB2: FILTER; R_1206
IC1: ATXMEGA128A1U-A; TQFP-100_14x14mm_Pitch0.5mm
MK1: Electret-mic; Eletret-mic-6x5
P1: CONN_02X02; Pin_Header_Straight_2x02
P2, P12, P13, P14, P16: CONN_01X02; Pin_Header_Straight_1x02
P3: PDI; Pin_Header_Straight_2x03
P4: PORT B; Pin_Header_Straight_2x05
P5: PORT J; Pin_Header_Straight_2x05
P6: PORT D; Pin_Header_Straight_2x05
P8: nRF8001 CON; Pin_Header_Straight_1x10
P9, P10, P11: MIC-CON-MONO; J2-connector
P15: CONN_01X02; Pin_Header_Angled_1x02
R1, R2, R33: 47k; R_0603
R3, R4: 15k; R_0603
R5, R12, R13, R14, R15, R16, R17, R19, R22, R23, R24, R26: 10K; R_0603
R6: LDR; Pin_Header_Straight_1x02
R7: 8k2; R_0603
R8, R9, R10, R11: 220; R_0603
R18, R20, R21, R39: 1M; R_0603
R25: 100K; R_0603
R27: 120k; R_0603
R28, R29, R30, R32, R36: 100k; R_0603
R31: 12k; R_0603
R34: 180k; R_0603
R35, R38: 10k; R_0603
R37: 22k; R_0603
SD1: uSD; uSD_5027_normal
SW1: SW_PUSH; 5mm-smd-button
SW2: SW_PUSH; 4.5mm-dip-button
U1, U3: LM35; TO-92_Molded_Narrow_Oval
U2: TPS71727; SC-70-5
U4: TPS71733; SC-70-5
U5: ADXL335; ADXL335_correto
U6: ADS1293; ADS1293-correto
U7: HDC1050
U8: OPT3001
U9: LM2665; DBV-PDSO-G6
U10: opa2333; SOIC8-PDSO_G8
VR1: 100k; Pin_Header_Straight_1x03
X1: 4.096MHz; Crystal_HC49-U_Vertical
X2: CRISTAL_16MHz; CRISTAL_16Mhz

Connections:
+BAT: C4.2, D1.2, P15.1, R1.1, U4.1, U4.3
/2Vcc: C47.1, C55.1, C56.1, C58.1, D6.1, P16.1, R30.1, R31.1, R38.1, U1.1, U3.1, U9.5, U10.8
/8_nRF: IC1.15, P8.8
/ACT_nRF: IC1.17, P8.6
/ADCA_REF: C3.2, C13.2, C14.2, IC1.95, P2.1, R6.1, U2.5, U5.14, U5.15
/ADCB_REF: C16.2, C17.2, IC1.5, P4.3
/ADC_A1: C10.2, IC1.96, R4.2
/ADC_A2: C9.2, IC1.97, R3.2
/ADC_A3: IC1.98, U5.12
/ADC_A4: IC1.99, U5.10
/ADC_A5: IC1.100, U5.8
/ADC_A6: C15.2, IC1.1, R7.1
/ADC_A7: C8.2, IC1.2, R1.2, R2.2
/ADC_B1: IC1.6, P4.4, R26.2
/ADC_B2: C52.1, C53.1, D8.1, IC1.7, P4.5, R32.1
/ADC_B3: IC1.8, P4.6
/ADC_B4: IC1.9, P4.7
/ADC_B5: IC1.10, P4.8
/ADC_B6: IC1.11, P4.9
/ADC_B7: IC1.12, P4.10
/INT_OPT: IC1.47, U8.5
/J0: IC1.65, P5.3
/J1: IC1.66, P5.4
/J2: IC1.67, P5.5
/J3: IC1.68, P5.6
/J4: IC1.69, P5.7
/J5: IC1.70, P5.8
/J6: IC1.71, P5.9
/J7: IC1.72, P5.10
/MISO_nRF: IC1.21, P8.2
/MISO_uSD: IC1.41, SD1.7
/MOSI-uSD: IC1.40, SD1.3
/MOSI_nRF: IC1.20, P8.3
/RDY_nRF: IC1.18, P8.5
/RESET: IC1.90, P3.5, R5.1, SW1.2
/RST_nRF: IC1.16, P8.7
/SCK-uSD: IC1.42, SD1.5
/SCK_nRF: IC1.22, P8.1
/SCL_HDC: IC1.36, R22.1, U7.6
/SCL_OPT: IC1.46, R24.2, U8.4
/SDA_HDC: IC1.35, R19.2, U7.1
/SDA_OPT: IC1.45, R23.2, U8.6
/malha: C33.2, P9.1, P9.2, P9.5, P10.1, P10.2, P10.5, P11.1, P11.2, P11.5, P12.2, P13.2, P14.2, R20.2
/xt1: IC1.91, R39.2, X2.1
/xt2: IC1.92, R39.1, X2.3
/~CS_nRF: IC1.19, P8.4
/~SS-uSD: IC1.39, SD1.2
GND: C1.1, C2.1, C3.1, C4.1, C5.1, C6.1, C8.1, C9.1, C10.1, C11.2, C12.2, C13.1, C14.1, C15.1, C16.1, C17.1, C23.2, C24.1, C25.1, C33.1, C35.2, C36.2, C37.2, C38.2, C39.2, C40.2, C41.2, C42.2, C43.2, C44.2, C45.2, C46.2, C47.2, C48.2, C53.2, C54.2, C55.2, C56.2, D1.1, D8.2, FB2.1, IC1.3, IC1.13, IC1.23, IC1.33, IC1.43, IC1.53, IC1.63, IC1.73, IC1.84, IC1.93, MK1.2, P1.3, P1.4, P2.2, P3.6, P4.2, P5.2, P6.2, P8.9, P15.2, P16.2, R2.1, R8.1, R9.1, R10.1, R11.1, R20.1, R29.1, R32.2, R34.2, R36.2, R37.1, SD1.6, SW1.1, SW2.1, U1.3, U2.2, U3.3, U4.2, U5.3, U5.5, U5.6, U5.7, U6.14, U7.2, U8.0, U8.2, U8.3, U9.2, U9.4, U10.4, VR1.2, VR1.3, X2.2
GNDA: C7.1, C20.2, C21.1, C22.2, C26.2, C27.2, C28.2, C29.2, C30.2, C31.2, C32.2, C57.2, FB2.2, U6.27
unnamed: C2.2, U2.4
unnamed: C5.2, U4.4
unnamed: C18.2, U6.24, X1.2
unnamed: C19.2, U6.23, X1.1
unnamed: C21.2, U6.26
unnamed: C26.1, R17.1, U6.1
unnamed: C27.1, R16.1, U6.2
unnamed: C28.1, R15.1, U6.3
unnamed: C29.1, R14.1, U6.4
unnamed: C30.1, R13.1, U6.5
unnamed: C31.1, R12.1, U6.6
unnamed: C32.1, U6.11, U6.12
unnamed: C34.1, R21.1, R25.1, U6.10
unnamed: C34.2, R21.2, U6.9
unnamed: C49.1, U9.3
unnamed: C49.2, U9.6
unnamed: C50.1, R27.1, U10.1, U10.5
unnamed: C50.2, C51.2, R27.2, U10.2
unnamed: C51.1, MK1.1, R31.2
unnamed: C52.2, D7.1, R28.1, R34.1
unnamed: C54.1, R30.2, R36.1, U10.3
unnamed: D2.1, IC1.76
unnamed: D2.2, R8.2
unnamed: D3.1, IC1.77
unnamed: D3.2, R9.2
unnamed: D4.1, IC1.78
unnamed: D4.2, R10.2
unnamed: D5.1, IC1.79
unnamed: D5.2, R11.2
unnamed: D7.2, R33.1, U10.7
unnamed: IC1.25, P6.3
unnamed: IC1.26, P6.4
unnamed: IC1.27, P6.5
unnamed: IC1.28, P6.6
unnamed: IC1.29, P6.7
unnamed: IC1.30, P6.8
unnamed: IC1.31, P6.9
unnamed: IC1.32, P6.10
unnamed: IC1.48, U6.20
unnamed: IC1.49, U6.16
unnamed: IC1.50, U6.18
unnamed: IC1.51, U6.19
unnamed: IC1.52, U6.17
unnamed: IC1.55, U6.15
unnamed: IC1.75, SW2.2
unnamed: IC1.89, P3.1
unnamed: P9.3, P9.4, R15.2
unnamed: P10.3, P10.4, R16.2
unnamed: P11.3, P11.4, R17.2
unnamed: P12.1, R12.2
unnamed: P13.1, R13.2
unnamed: P14.1, R14.2
unnamed: R3.1, U1.2
unnamed: R4.1, U3.2
unnamed: R6.2, R7.2, VR1.1
unnamed: R18.2, U6.13
unnamed: R25.2, U6.8
unnamed: R26.1, R28.2, R29.2
unnamed: R33.2, R35.1, U10.6
unnamed: R35.2, R37.2, R38.2
VCC: C1.2, C6.2, C11.1, C12.1, C23.1, C24.2, C25.2, C35.1, C36.1, C37.1, C38.1, C39.1, C40.1, C41.1, C42.1, C43.1, C44.1, C45.1, C46.1, C48.1, C58.2, D6.2, FB1.1, IC1.4, IC1.14, IC1.24, IC1.34, IC1.44, IC1.54, IC1.64, IC1.74, IC1.83, IC1.94, P1.1, P1.2, P3.2, P4.1, P5.1, P6.1, P8.10, R5.2, R18.1, R19.1, R22.2, R23.1, R24.1, SD1.4, U2.1, U2.3, U4.5, U6.22, U7.5, U8.1, U9.1
aVDD: C7.2, C18.1, C19.1, C20.1, C22.1, C57.1, FB1.2, U6.28

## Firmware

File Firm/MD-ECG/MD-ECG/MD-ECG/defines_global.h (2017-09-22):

/*
 * defines_global.h
 *
 * Created: 16-Mar-16 10:03:14
 *  Author: Felipe Schneider
 */ 


#ifndef DEFINES_GLOBAL_H_
#define DEFINES_GLOBAL_H_

#define lo8(x) ((uint8_t)((x) & 0xff))
#define hi8(x) ((uint8_t)((x & 0xff00)>>8))
#define hi16(x) ((uint8_t)((x & 0xff0000)>>16))
#define hi24(x) ((uint8_t)((x & 0xff000000)>>24))

#define F_CPU			32000000UL		//CPU CLOCK (for delay lib)
//#define XT_CLOCK						//Enables the external XT init functions (btw 12 an 16MHz with the actual settings)
//#define PLL_CLOCK						//Enables the PLL init functions (external xt necessary)
#define RC_32_CLOCK						//Enables the internal resonator init functions (32MHz with PLL with the actual settings)
#define	SERIAL_E0						//Enables the Uart D0 init functions
#define SPI_D0
#define ZERO_ASCII		48

#define READ_ADS	0x80
#define WRITE_ADS	0x00

#define	VALOR_A_TENSAO	0.001340814115672
#define	VALOR_B_TENSAO	-0.294399010115506

#define HEADER_1	0x53	//S em ascii
#define HEADER_2	0x54	//T em ascii

// Connected to port A
#define REFA_PIN	PIN0_bm
#define BAT_DIV		PIN1_bm
#define XOUT_ADXL	PIN2_bm
#define YOUT_ADXL	PIN3_bm
#define ZOUT_ADXL	PIN4_bm
#define ZOUT_ADXL_2	PIN5_bm
#define YOUT_ADXL_2	PIN6_bm
#define XOUT_ADXL_2	PIN7_bm

// Connected to port B
#define ZOUT_ADXL_3	PIN1_bm
#define YOUT_ADXL_3	PIN2_bm
#define XOUT_ADXL_3	PIN3_bm

// Connected to port C
#define SS_uSD		PIN4_bm
#define MOSI_uSD	PIN5_bm
#define MISO_uSD	PIN6_bm
#define SCK_uSD		PIN7_bm

// Connected to port D
#define RST_nRF		PIN1_bm
#define ACT_nRF		PIN2_bm
#define RDY_nRF		PIN3_bm
#define CS_nRF		PIN4_bm
#define MOSI_nRF	PIN5_bm
#define MISO_nRF	PIN6_bm
#define SCK_nRF		PIN7_bm

// Connected to port E
#define UART_RX		PIN2_bm
#define UART_TX		PIN3_bm

#define LED3		PIN5_bm
#define LED2		PIN6_bm
#define SINC_PIN	PIN7_bm

// Connected to port F
#define SDA_OPT		PIN0_bm
#define SCL_OPT		PIN1_bm
#define DRDYB_ADS	PIN2_bm
#define ALARM_ADS	PIN3_bm
#define SS_ADS		PIN4_bm
#define MOSI_ADS	PIN5_bm
#define MISO_ADS	PIN6_bm
#define SCK_ADS		PIN7_bm

#endif /* DEFINES_GLOBAL_H_ */

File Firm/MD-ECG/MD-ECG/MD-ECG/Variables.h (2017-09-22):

/*
 * Variables.h
 *
 * Created: 29/03/2016 17:34:00
 *  Author: Win7
 */ 


#ifndef VARIABLES_H_
#define VARIABLES_H_
#include <avr/io.h>

//Todas as amostras dever ser organizadas em um único vetor a fim de serem transmitidas para o µSD
//assim sendo, devo definir offsets para o inicio de cada variavel dentro do vetor g_buffer_uSD
#define HEADER_OFFSET		0
#define ECG_OFFSET			2

#define ACC_X_OFFSET		1202
#define ACC_Y_OFFSET		1282
#define ACC_Z_OFFSET		1362

#define ACC_X_2_OFFSET		1442
#define ACC_Y_2_OFFSET		1522
#define ACC_Z_2_OFFSET		1602

#define ACC_X_3_OFFSET		1682
#define ACC_Y_3_OFFSET		1762
#define ACC_Z_3_OFFSET		1842

#define BAT_VAL_OFFSET		1922
#define CRC_OFFSET			1924
#define BUFFER_SIZE			1926

extern uint8_t g_buffer_uSD[BUFFER_SIZE], g_buffer_uSD_2[BUFFER_SIZE];	//buffers that will save data into µSD
extern uint8_t gf_buffer_indicator;		//indicates which buffer is active, if 1 we are using the g_buffer_uSD
extern uint8_t gf_start_transmission;	//indicates that we must start a transmission to µSD

 
extern uint8_t g_bat_ad;		//value returned by the ad conversion of the battery
extern uint8_t gc_bat;			//counts how many samples of ADC battery values happened and were saved

extern uint16_t g_acc_x, g_acc_y, g_acc_z; //accelerometer results
extern uint8_t gc_acc;			//counts how many samples of accelerometer values happened and were saved
extern uint16_t g_acc_x_2, g_acc_y_2, g_acc_z_2; //accelerometer results
extern uint8_t gc_acc_2;			//counts how many samples of accelerometer values happened and were saved
extern uint16_t g_acc_x_3, g_acc_y_3, g_acc_z_3; //accelerometer results
extern uint8_t gc_acc_3;			//counts how many samples of accelerometer values happened and were saved
extern uint8_t f_select_acc;		//changes btw acc2 and acc3

extern uint8_t g_ads_ecg_1, g_ads_ecg_2, g_ads_ecg_3; //bytes from ADS, 1 is the most significant
extern uint16_t gc_ecg;			//counts how many samples of ADS EOG values happened and were saved

extern uint8_t g_error;

extern uint8_t g_patient_number;	//number of the patient, goes up to 9 and depends of the pre-existing file
#endif /* VARIABLES_H_ */

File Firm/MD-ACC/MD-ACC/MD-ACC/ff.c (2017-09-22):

/*----------------------------------------------------------------------------/
/  FatFs - FAT file system module  R0.11                 (C)ChaN, 2015
/-----------------------------------------------------------------------------/
/ FatFs module is a free software that opened under license policy of
/ following conditions.
/
/ Copyright (C) 2015, ChaN, all right reserved.
/
/ 1. Redistributions of source code must retain the above copyright notice,
/    this condition and the following disclaimer.
/
/ This software is provided by the copyright holder and contributors "AS IS"
/ and any warranties related to this software are DISCLAIMED.
/ The copyright owner or contributors be NOT LIABLE for any damages caused
/ by use of this software.
/----------------------------------------------------------------------------*/


#include "ff.h"			/* Declarations of FatFs API */
#include "diskio.h"		/* Declarations of disk I/O functions */
#include "MMC.h"

/*--------------------------------------------------------------------------

   Module Private Definitions

---------------------------------------------------------------------------*/

#if _FATFS != 32020	/* Revision ID */
#error Wrong include file (ff.h).
#endif


/* Reentrancy related */
#if _FS_REENTRANT
#if _USE_LFN == 1
#error Static LFN work area cannot be used at thread-safe configuration
#endif
#define	ENTER_FF(fs)		{ if (!lock_fs(fs)) return FR_TIMEOUT; }
#define	LEAVE_FF(fs, res)	{ unlock_fs(fs, res); return res; }
#else
#define	ENTER_FF(fs)
#define LEAVE_FF(fs, res)	return res
#endif

#define	ABORT(fs, res)		{ fp->err = (BYTE)(res); LEAVE_FF(fs, res); }


/* Definitions of sector size */
#if (_MAX_SS < _MIN_SS) || (_MAX_SS != 512 && _MAX_SS != 1024 && _MAX_SS != 2048 && _MAX_SS != 4096) || (_MIN_SS != 512 && _MIN_SS != 1024 && _MIN_SS != 2048 && _MIN_SS != 4096)
#error Wrong sector size configuration
#endif
#if _MAX_SS == _MIN_SS
#define	SS(fs)	((UINT)_MAX_SS)	/* Fixed sector size */
#else
#define	SS(fs)	((fs)->ssize)	/* Variable sector size */
#endif


/* Timestamp feature */
#if _FS_NORTC == 1
#if _NORTC_YEAR < 1980 || _NORTC_YEAR > 2107 || _NORTC_MON < 1 || _NORTC_MON > 12 || _NORTC_MDAY < 1 || _NORTC_MDAY > 31
#error Invalid _FS_NORTC settings
#endif
#define GET_FATTIME()	((DWORD)(_NORTC_YEAR - 1980) << 25 | (DWORD)_NORTC_MON << 21 | (DWORD)_NORTC_MDAY << 16)
#else
#define GET_FATTIME()	get_fattime()
#endif


/* File access control feature */
#if _FS_LOCK
#if _FS_READONLY
#error _FS_LOCK must be 0 at read-only configuration
#endif
typedef struct {
	FATFS *fs;		/* Object ID 1, volume (NULL:blank entry) */
	DWORD clu;		/* Object ID 2, directory (0:root) */
	WORD idx;		/* Object ID 3, directory index */
	WORD ctr;		/* Object open counter, 0:none, 0x01..0xFF:read mode open count, 0x100:write mode */
} FILESEM;
#endif



/* DBCS code ranges and SBCS extend character conversion table */

#if _CODE_PAGE == 932	/* Japanese Shift-JIS */
#define _DF1S	0x81	/* DBC 1st byte range 1 start */
#define _DF1E	0x9F	/* DBC 1st byte range 1 end */
#define _DF2S	0xE0	/* DBC 1st byte range 2 start */
#define _DF2E	0xFC	/* DBC 1st byte range 2 end */
#define _DS1S	0x40	/* DBC 2nd byte range 1 start */
#define _DS1E	0x7E	/* DBC 2nd byte range 1 end */
#define _DS2S	0x80	/* DBC 2nd byte range 2 start */
#define _DS2E	0xFC	/* DBC 2nd byte range 2 end */

#elif _CODE_PAGE == 936	/* Simplified Chinese GBK */
#define _DF1S	0x81
#define _DF1E	0xFE
#define _DS1S	0x40
#define _DS1E	0x7E
#define _DS2S	0x80
#define _DS2E	0xFE

#elif _CODE_PAGE == 949	/* Korean */
#define _DF1S	0x81
#define _DF1E	0xFE
#define _DS1S	0x41
#define _DS1E	0x5A
#define _DS2S	0x61
#define _DS2E	0x7A
#define _DS3S	0x81
#define _DS3E	0xFE

#elif _CODE_PAGE == 950	/* Traditional Chinese Big5 */
#define _DF1S	0x81
#define _DF1E	0xFE
#define _DS1S	0x40
#define _DS1E	0x7E
#define _DS2S	0xA1
#define _DS2E	0xFE

#elif _CODE_PAGE == 437	/* U.S. (OEM) */
#define _DF1S	0
#define _EXCVT {0x80,0x9A,0x90,0x41,0x8E,0x41,0x8F,0x80,0x45,0x45,0x45,0x49,0x49,0x49,0x8E,0x8F,0x90,0x92,0x92,0x4F,0x99,0x4F,0x55,0x55,0x59,0x99,0x9A,0x9B,0x9C,0x9D,0x9E,0x9F, \
				0x41,0x49,0x4F,0x55,0xA5,0xA5,0xA6,0xA7,0xA8,0xA9,0xAA,0xAB,0xAC,0x21,0xAE,0xAF,0xB0,0xB1,0xB2,0xB3,0xB4,0xB5,0xB6,0xB7,0xB8,0xB9,0xBA,0xBB,0xBC,0xBD,0xBE,0xBF, \
				0xC0,0xC1,0xC2,0xC3,0xC4,0xC5,0xC6,0xC7,0xC8,0xC9,0xCA,0xCB,0xCC,0xCD,0xCE,0xCF,0xD0,0xD1,0xD2,0xD3,0xD4,0xD5,0xD6,0xD7,0xD8,0xD9,0xDA,0xDB,0xDC,0xDD,0xDE,0xDF, \
				0xE0,0xE1,0xE2,0xE3,0xE4,0xE5,0xE6,0xE7,0xE8,0xE9,0xEA,0xEB,0xEC,0xED,0xEE,0xEF,0xF0,0xF1,0xF2,0xF3,0xF4,0xF5,0xF6,0xF7,0xF8,0xF9,0xFA,0xFB,0xFC,0xFD,0xFE,0xFF}

#elif _CODE_PAGE == 720	/* Arabic (OEM) */
#define _DF1S	0
#define _EXCVT {0x80,0x81,0x45,0x41,0x84,0x41,0x86,0x43,0x45,0x45,0x45,0x49,0x49,0x8D,0x8E,0x8F,0x90,0x92,0x92,0x93,0x94,0x95,0x49,0x49,0x98,0x99,0x9A,0x9B,0x9C,0x9D,0x9E,0x9F, \
				0xA0,0xA1,0xA2,0xA3,0xA4,0xA5,0xA6,0xA7,0xA8,0xA9,0xAA,0xAB,0xAC,0xAD,0xAE,0xAF,0xB0,0xB1,0xB2,0xB3,0xB4,0xB5,0xB6,0xB7,0xB8,0xB9,0xBA,0xBB,0xBC,0xBD,0xBE,0xBF, \
				0xC0,0xC1,0xC2,0xC3,0xC4,0xC5,0xC6,0xC7,0xC8,0xC9,0xCA,0xCB,0xCC,0xCD,0xCE,0xCF,0xD0,0xD1,0xD2,0xD3,0xD4,0xD5,0xD6,0xD7,0xD8,0xD9,0xDA,0xDB,0xDC,0xDD,0xDE,0xDF, \
				0xE0,0xE1,0xE2,0xE3,0xE4,0xE5,0xE6,0xE7,0xE8,0xE9,0xEA,0xEB,0xEC,0xED,0xEE,0xEF,0xF0,0xF1,0xF2,0xF3,0xF4,0xF5,0xF6,0xF7,0xF8,0xF9,0xFA,0xFB,0xFC,0xFD,0xFE,0xFF}

#elif _CODE_PAGE == 737	/* Greek (OEM) */
#define _DF1S	0
#define _EXCVT {0x80,0x81,0x82,0x83,0x84,0x85,0x86,0x87,0x88,0x89,0x8A,0x8B,0x8C,0x8D,0x8E,0x8F,0x90,0x92,0x92,0x93,0x94,0x95,0x96,0x97,0x80,0x81,0x82,0x83,0x84,0x85,0x86,0x87, \
				0x88,0x89,0x8A,0x8B,0x8C,0x8D,0x8E,0x8F,0x90,0x91,0xAA,0x92,0x93,0x94,0x95,0x96,0xB0,0xB1,0xB2,0xB3,0xB4,0xB5,0xB6,0xB7,0xB8,0xB9,0xBA,0xBB,0xBC,0xBD,0xBE,0xBF, \
				0xC0,0xC1,0xC2,0xC3,0xC4,0xC5,0xC6,0xC7,0xC8,0xC9,0xCA,0xCB,0xCC,0xCD,0xCE,0xCF,0xD0,0xD1,0xD2,0xD3,0xD4,0xD5,0xD6,0xD7,0xD8,0xD9,0xDA,0xDB,0xDC,0xDD,0xDE,0xDF, \
				0x97,0xEA,0xEB,0xEC,0xE4,0xED,0xEE,0xE7,0xE8,0xF1,0xEA,0xEB,0xEC,0xED,0xEE,0xEF,0xF0,0xF1,0xF2,0xF3,0xF4,0xF5,0xF6,0xF7,0xF8,0xF9,0xFA,0xFB,0xFC,0xFD,0xFE,0xFF}

#elif _CODE_PAGE == 775	/* Baltic (OEM) */
#define _DF1S	0
#define _EXCVT {0x80,0x9A,0x91,0xA0,0x8E,0x95,0x8F,0x80,0xAD,0xED,0x8A,0x8A,0xA1,0x8D,0x8E,0x8F,0x90,0x92,0x92,0xE2,0x99,0x95,0x96,0x97,0x97,0x99,0x9A,0x9D,0x9C,0x9D,0x9E,0x9F, \
				0xA0,0xA1,0xE0,0xA3,0xA3,0xA5,0xA6,0xA7,0xA8,0xA9,0xAA,0xAB,0xAC,0xAD,0xAE,0xAF,0xB0,0xB1,0xB2,0xB3,0xB4,0xB5,0xB6,0xB7,0xB8,0xB9,0xBA,0xBB,0xBC,0xBD,0xBE,0xBF, \
				0xC0,0xC1,0xC2,0xC3,0xC4,0xC5,0xC6,0xC7,0xC8,0xC9,0xCA,0xCB,0xCC,0xCD,0xCE,0xCF,0xB5,0xB6,0xB7,0xB8,0xBD,0xBE,0xC6,0xC7,0xA5,0xD9,0xDA,0xDB,0xDC,0xDD,0xDE,0xDF, \
				0xE0,0xE1,0xE2,0xE3,0xE5,0xE5,0xE6,0xE3,0xE8,0xE8,0xEA,0xEA,0xEE,0xED,0xEE,0xEF,0xF0,0xF1,0xF2,0xF3,0xF4,0xF5,0xF6,0xF7,0xF8,0xF9,0xFA,0xFB,0xFC,0xFD,0xFE,0xFF}

#elif _CODE_PAGE == 850	/* Multilingual Latin 1 (OEM) */
#define _DF1S	0
#define _EXCVT {0x80,0x9A,0x90,0xB6,0x8E,0xB7,0x8F,0x80,0xD2,0xD3,0xD4,0xD8,0xD7,0xDE,0x8E,0x8F,0x90,0x92,0x92,0xE2,0x99,0xE3,0xEA,0xEB,0x59,0x99,0x9A,0x9D,0x9C,0x9D,0x9E,0x9F, \
				0xB5,0xD6,0xE0,0xE9,0xA5,0xA5,0xA6,0xA7,0xA8,0xA9,0xAA,0xAB,0xAC,0x21,0xAE,0xAF,0xB0,0xB1,0xB2,0xB3,0xB4,0xB5,0xB6,0xB7,0xB8,0xB9,0xBA,0xBB,0xBC,0xBD,0xBE,0xBF, \
				0xC0,0xC1,0xC2,0xC3,0xC4,0xC5,0xC7,0xC7,0xC8,0xC9,0xCA,0xCB,0xCC,0xCD,0xCE,0xCF,0xD0,0xD1,0xD2,0xD3,0xD4,0xD5,0xD6,0xD7,0xD8,0xD9,0xDA,0xDB,0xDC,0xDD,0xDE,0xDF, \
				0xE0,0xE1,0xE2,0xE3,0xE5,0xE5,0xE6,0xE7,0xE7,0xE9,0xEA,0xEB,0xED,0xED,0xEE,0xEF,0xF0,0xF1,0xF2,0xF3,0xF4,0xF5,0xF6,0xF7,0xF8,0xF9,0xFA,0xFB,0xFC,0xFD,0xFE,0xFF}

#elif _CODE_PAGE == 852	/* Latin 2 (OEM) */
#define _DF1S	0
#define _EXCVT {0x80,0x9A,0x90,0xB6,0x8E,0xDE,0x8F,0x80,0x9D,0xD3,0x8A,0x8A,0xD7,0x8D,0x8E,0x8F,0x90,0x91,0x91,0xE2,0x99,0x95,0x95,0x97,0x97,0x99,0x9A,0x9B,0x9B,0x9D,0x9E,0x9F, \
				0xB5,0xD6,0xE0,0xE9,0xA4,0xA4,0xA6,0xA6,0xA8,0xA8,0xAA,0x8D,0xAC,0xB8,0xAE,0xAF,0xB0,0xB1,0xB2,0xB3,0xB4,0xB5,0xB6,0xB7,0xB8,0xB9,0xBA,0xBB,0xBC,0xBD,0xBD,0xBF, \
				0xC0,0xC1,0xC2,0xC3,0xC4,0xC5,0xC6,0xC6,0xC8,0xC9,0xCA,0xCB,0xCC,0xCD,0xCE,0xCF,0xD1,0xD1,0xD2,0xD3,0xD2,0xD5,0xD6,0xD7,0xB7,0xD9,0xDA,0xDB,0xDC,0xDD,0xDE,0xDF, \
				0xE0,0xE1,0xE2,0xE3,0xE3,0xD5,0xE6,0xE6,0xE8,0xE9,0xE8,0xEB,0xED,0xED,0xDD,0xEF,0xF0,0xF1,0xF2,0xF3,0xF4,0xF5,0xF6,0xF7,0xF8,0xF9,0xFA,0xEB,0xFC,0xFC,0xFE,0xFF}

#elif _CODE_PAGE == 855	/* Cyrillic (OEM) */
#define _DF1S	0
#define _EXCVT {0x81,0x81,0x83,0x83,0x85,0x85,0x87,0x87,0x89,0x89,0x8B,0x8B,0x8D,0x8D,0x8F,0x8F,0x91,0x91,0x93,0x93,0x95,0x95,0x97,0x97,0x99,0x99,0x9B,0x9B,0x9D,0x9D,0x9F,0x9F, \
				0xA1,0xA1,0xA3,0xA3,0xA5,0xA5,0xA7,0xA7,0xA9,0xA9,0xAB,0xAB,0xAD,0xAD,0xAE,0xAF,0xB0,0xB1,0xB2,0xB3,0xB4,0xB6,0xB6,0xB8,0xB8,0xB9,0xBA,0xBB,0xBC,0xBE,0xBE,0xBF, \
				0xC0,0xC1,0xC2,0xC3,0xC4,0xC5,0xC7,0xC7,0xC8,0xC9,0xCA,0xCB,0xCC,0xCD,0xCE,0xCF,0xD1,0xD1,0xD3,0xD3,0xD5,0xD5,0xD7,0xD7,0xDD,0xD9,0xDA,0xDB,0xDC,0xDD,0xE0,0xDF, \
				0xE0,0xE2,0xE2,0xE4,0xE4,0xE6,0xE6,0xE8,0xE8,0xEA,0xEA,0xEC,0xEC,0xEE,0xEE,0xEF,0xF0,0xF2,0xF2,0xF4,0xF4,0xF6,0xF6,0xF8,0xF8,0xFA,0xFA,0xFC,0xFC,0xFD,0xFE,0xFF}

#elif _CODE_PAGE == 857	/* Turkish (OEM) */
#define _DF1S	0
#define _EXCVT {0x80,0x9A,0x90,0xB6,0x8E,0xB7,0x8F,0x80,0xD2,0xD3,0xD4,0xD8,0xD7,0x98,0x8E,0x8F,0x90,0x92,0x92,0xE2,0x99,0xE3,0xEA,0xEB,0x98,0x99,0x9A,0x9D,0x9C,0x9D,0x9E,0x9E, \
				0xB5,0xD6,0xE0,0xE9,0xA5,0xA5,0xA6,0xA6,0xA8,0xA9,0xAA,0xAB,0xAC,0x21,0xAE,0xAF,0xB0,0xB1,0xB2,0xB3,0xB4,0xB5,0xB6,0xB7,0xB8,0xB9,0xBA,0xBB,0xBC,0xBD,0xBE,0xBF, \
				0xC0,0xC1,0xC2,0xC3,0xC4,0xC5,0xC7,0xC7,0xC8,0xC9,0xCA,0xCB,0xCC,0xCD,0xCE,0xCF,0xD0,0xD1,0xD2,0xD3,0xD4,0xD5,0xD6,0xD7,0xD8,0xD9,0xDA,0xDB,0xDC,0xDD,0xDE,0xDF, \
				0xE0,0xE1,0xE2,0xE3,0xE5,0xE5,0xE6,0xE7,0xE8,0xE9,0xEA,0xEB,0xDE,0x59,0xEE,0xEF,0xF0,0xF1,0xF2,0xF3,0xF4,0xF5,0xF6,0xF7,0xF8,0xF9,0xFA,0xFB,0xFC,0xFD,0xFE,0xFF}

#elif _CODE_PAGE == 858	/* Multilingual Latin 1 + Euro (OEM) */
#define _DF1S	0
#define _EXCVT {0x80,0x9A,0x90,0xB6,0x8E,0xB7,0x8F,0x80,0xD2,0xD3,0xD4,0xD8,0xD7,0xDE,0x8E,0x8F,0x90,0x92,0x92,0xE2,0x99,0xE3,0xEA,0xEB,0x59,0x99,0x9A,0x9D,0x9C,0x9D,0x9E,0x9F, \
				0xB5,0xD6,0xE0,0xE9,0xA5,0xA5,0xA6,0xA7,0xA8,0xA9,0xAA,0xAB,0xAC,0x21,0xAE,0xAF,0xB0,0xB1,0xB2,0xB3,0xB4,0xB5,0xB6,0xB7,0xB8,0xB9,0xBA,0xBB,0xBC,0xBD,0xBE,0xBF, \
				0xC0,0xC1,0xC2,0xC3,0xC4,0xC5,0xC7,0xC7,0xC8,0xC9,0xCA,0xCB,0xCC,0xCD,0xCE,0xCF,0xD1,0xD1,0xD2,0xD3,0xD4,0xD5,0xD6,0xD7,0xD8,0xD9,0xDA,0xDB,0xDC,0xDD,0xDE,0xDF, \
				0xE0,0xE1,0xE2,0xE3,0xE5,0xE5,0xE6,0xE7,0xE7,0xE9,0xEA,0xEB,0xED,0xED,0xEE,0xEF,0xF0,0xF1,0xF2,0xF3,0xF4,0xF5,0xF6,0xF7,0xF8,0xF9,0xFA,0xFB,0xFC,0xFD,0xFE,0xFF}
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
